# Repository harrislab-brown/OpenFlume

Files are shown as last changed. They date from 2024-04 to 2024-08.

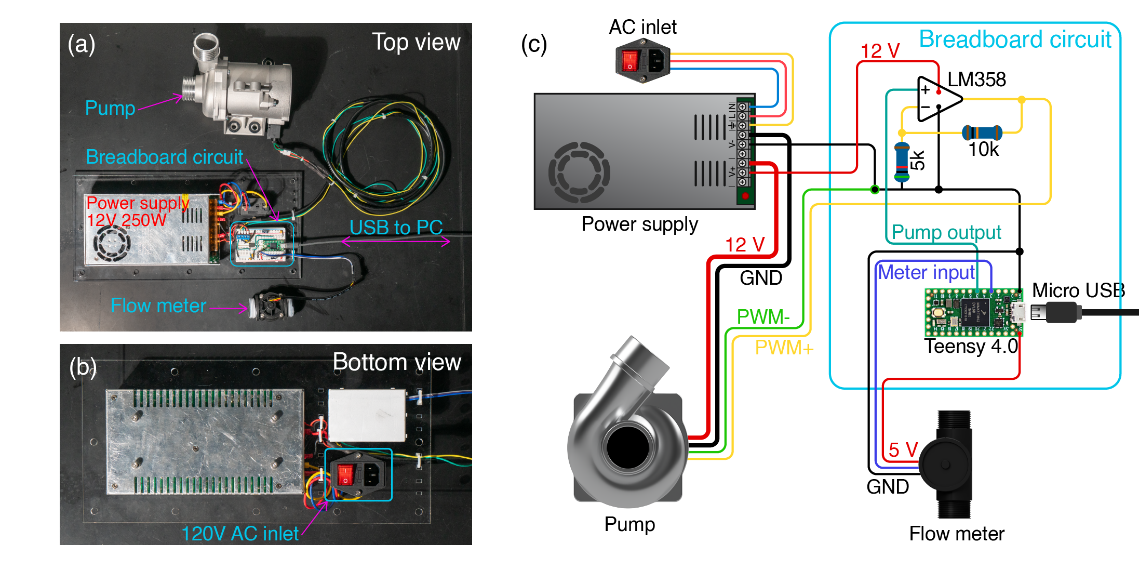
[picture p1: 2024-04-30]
Wiring Diagram/electronics_diagram3.png

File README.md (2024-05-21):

# OpenFlume
Low-cost benchtop laboratory flume for research and education with full build documentation released under an open-hardware license.

## What is OpenFlume?
OpenFlume is an open channel flume that features a 5x5cm flow test-section with free stream speeds upto 50 cm/s. It is as small as it can be while still allowing for ample flow conditioning prior to the test section. It has been fully characterized using Particle
Image Velocimetry. It is designed to be buildable with a range of tool access and skill levels. It uses the minimum viable product for its construction, keeping costs low without sacrificing quality. It is fully documented, so you 
can follow our instructions and build an OpenFlume to suit your needs. 

OpenFlume was designed by members of the Harris Lab and Brown University for experiments related to drag at the interface. To conduct these experiments, the lab needed a well controlled and uniform flow with low surface deviation. 
When looking at the commercial landscape for small scale flumes, the few small scale flumes that were available were expensive and lacked the full characterization needed for the lab to be confident in their direct applicability to research. 

## License:
OpenFlume is licensed under the CC BY-SA 4.0 Creative Commons license.

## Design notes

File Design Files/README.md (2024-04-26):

# OpenFlume

All of the 3D CAD and 2D cut files associated with the OpenFlume project.

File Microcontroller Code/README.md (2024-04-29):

# OpenFlume

This arduino sketch has been tested on a Teensy4.0 development board.
To use this code, follow the wiring diagram from the OpenFlume paper and make all appropriate connections with the Teensy. The Arduino IDE 2.x
has the ability to add additional board manager repositories. Follow the guide found at [PJRC Teensy4.0 Tutorial](https://www.pjrc.com/teensy/tutorial.html)
to get the Arduino IDE set up to flash the Teensy. Downlad the flume_controller.ino file and put it in a folder with the name flume_controller. This should allow you to open the arduino project in the IDE, compile, and flash the code.

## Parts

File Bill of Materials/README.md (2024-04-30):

# OpenFlume

Bill of materials for each subsystem can be found here. Open the .html files in a browser to view a static version of the BOM spreadsheets,
or find the same information in the .xlsx workbook for easier editability.

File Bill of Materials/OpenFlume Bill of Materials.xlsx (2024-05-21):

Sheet: Plumbing
Designator | Component | Quantity | Cost per Unit ($) | Total Price ($) | Source of Material | McMaster Carr Item Number
Plumbing | 1” Braided Vinyl Tubing | 4 ft | ($3.28 /ft.) | $13.12 | Home Depot
Plumbing | 1.5” Braided Vinyl Tubing | 4 ft | ($4.75 /ft.) | $19.00 | Home Depot
Plumbing | Bulkhead Fitting 1” NPT Female Thread 304 Stainless Steel Thru-bulk Fitting | 2 | ~10.00 | $19.99 | Amazon
Plumbing | PVC Barbed Tee Fitting - 1 PVC Tee Barb Fitting | 1 | $9.95 | $9.95 | Amazon
Plumbing | 1” NPT Gate Valve | 1 | $15.34 | $15.34 | Home Depot
Plumbing | High-Pressure Plastic Fitting (1.5” Barbed Male to 1.5” NPT Female) | 2 | $16.42 | $32.84 | McMaster Carr | 48315K113
Plumbing | High-Pressure Plastic Fitting (1.5” Barbed Male to 1” Barbed Male) | 2 | $8.01 | $16.02 | McMaster Carr | 48315K75
Plumbing | High-Pressure Plastic Fitting (1” Barbed Pipe × 1” NPT Male Threaded Pipe) | 4 | $2.47 | $9.88 | McMaster Carr | 48315K93
Plumbing | 1/2" Wide Teflon Tape | 1 | $3.97 | $3.97 | Amazon
Plumbing | Stainless Steel Hose Clamps (1 inch to 2 inch diameter) | 1 | $9.99 | $9.99 | Amazon
 |  |  | Total: | $150.10

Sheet: Electronics
Designator | Component | Quantity | Cost per Unit ($) | Total Price ($) | Source of Material | Part Number
Electronics | 1.5” Water Flow Sensor 5-150LPM | 1 | $26.99 | $26.99 | Amazon
Electronics | Teensy4.0 | 1 | $28.50 | $28.50 | Digikey | 1568-DEV-16997-ND
Electronics | S-250-12 Power Supply | 1 | $23.99 | $23.99 | Amazon
Electronics | LM358N Op-Amp | 1 | $0.89 | $0.89 | Digikey | LM358NNS/NOPB-ND
Electronics | Aftermarket CWA-200 BMW Coolant Pump | 1 | $118.99 | $118.99 | Amazon
Electronics | 15A 250V Rocker Switch Power Socket Inlet | 1 | $7.99 | $7.99 | Amazon
Electronics | Resistor Assortment 1/4W | 1 | $9.99 | $9.99 | Amazon
Electronics | Ceramic Capacitor Assortment | 1 | $9.99 | $9.99 | Amazon
Electronics | 14 AWG Silicone Wire 20' | 1 | $9.88 | $9.88 | Amazon
Electronics | Solderless Breadboard | 1 | $6.99 | $6.99 | Amazon
Electronics | Breadboard Hookup Wire assortment | 1 | $14.58 | $14.58 | Amazon
Electronics | Ring Terminal Assortment | 1 | $8.98 | $8.98 | Amazon
Electronics | Breadboard Screw Terminals | 1 | $8.99 | $8.99 | Amazon
Electronics | Micro USB Cable | 1 | $3.99 | $3.99 | Amazon
 |  | Total: | $280.74

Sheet: Aluminum Substructure
Designator | Component | Quantity | Cost per Unit ($) | Total Price ($) | Source of Material | McMaster Item Number | Material Type
Substructure | Silver Corner Surface Bracket for 1” High Single Rail | 10 | $11.60 | $116.00 | McMaster Carr | 47065T267
Substructure | Silver Flush 90 Degree Angle Bracket for 1” High Rail | 2 | $17.05 | $34.10 | McMaster Carr | 3136N157
Substructure | Silver Corner Surface Bracket 4” Long | 2 | $30.60 | $61.20 | McMaster Carr | 47065T274
Substructure | 1" Long for 1" High Rail T-Slotted Framing | 4 | $7.92 | $31.68 | McMaster Carr | 47065T236
Substructure | M5 x 0.8 mm Thread, 45 mm Long | 2 | $8.46 | $16.92 | McMaster Carr | 91292A195 | look up how many come with each order
Substructure | M5 x 0.8 mm Thread | 1 | $9.77 | $9.77 | McMaster Carr | 91828A241 | look up how many come with each order
Substructure | 18-8 Washer for M5 Screw Size, 5.300 mm ID, 9.000 mm OD | 1 | $4.00 | $4.00 | McMaster Carr | 98689A114 | look up how many come with each order
Substructure | 12” 1010-S from 80/20 | 4 | $6.99 | $27.96 | 80/20
Substructure | 5” (127 mm) 1010-S | 8 | $4.54 | $36.32
Substructure | 25” (635 mm) 1010-S | 2 | $11.54 | $23.08 | 80/20
Substructure | 21” (533.4 mm) 1010-S | 2 | $10.14 | $20.28 | 80/20
Substructure | 6.67” (169.42 mm) 1010-S | 2 | $5.12 | $10.24 | 80/20
Substructure | 8” (203.2 mm) 1020-S | 2 | $7.75 | $15.50 | 80/20
Substructure | 10” (254 mm) 1010-S | 4 | $6.29 | $25.16 | 80/20
 |  | Total: | $141.77

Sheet: Flume Body
Designator | Component | Quantity | Cost per Unit ($) | Total Price ($) | Source of Material | McMaster Item Number | Material Type
Flume Body | Plastic Straws | 1 | $8.99 | $8.99 | Donation |  | for flow straightening honeycomb
Flume Body | 9mm Thick Acrylic Sheet 96″ x 48″ | 1 | $190.00 | $190.00 | Polymershapes
Flume Body | Oil-Resistant Buna-N O-Ring Cord Stock, 3 mm Wide | 3 ft | $0.45/foot | $1.35 | McMaster Carr | 9679K14 | For o-rings at Flume flanges
Flume Body | 50A 0.5mm Thick Neoprene Sheet 12" × 12" | 1 | $6.71 | $6.71 | McMaster Carr | 85785K21 | For rubber washers at outlet tank flange
Flume Body | 5.5 mm Acrylic Sheet (48" x 24") | 2 | $66.40 | $132.80 | Canal Plastics
Flume Body | Weld-On #4 Adhesive (Pint) | 1 | $26.16 | $26.16 | Amazon
Flume Body | Wet Sandpaper Set | 1 | $12.99 | $12.99 | Amazon |  | Mimum grit of 60 needed, maximum grit of 2000 needed
Flume Body | 3 mm Acrylic Sheet (48" x 24") | 1 | $38.40 | $38.40 | Canal Plastics
Flume Body | Super Glue (25 gram) | 1 | $8.57 | $8.57 | Amazon
Flume Body | Masking Tape | 1 | $3.50 | $3.50 | Amazon
Flume Body | Stainless Steel M4 x 8 mm Screws | 1 | $8.18 (pack of 100) | $8.18 | McMaster | 91292A108 | for securing inlet diffuser - check length
Flume Body | Woven Wire Mesh Screen (20 mesh) | 1 | $6.99 | $6.99 | Amazon
Flume Body | Novus Plastic Polish Set (#1,#2,#3 2 ounce bottles) | 1 | $12.75 | $12.75 | Amazon
Flume Body | Stainless Steel M3 x 12 mm Screws | 1 | 6 (pack of 100) | $6.00 | McMaster Carr | 91292A114 | for securing mesh gate
Flume Body | Stainless Steel M5 x 45 mm Screws | 2 | 8.46 (pack of 25) | $16.92 | McMaster Carr | 91292A195 | for joining flume subassemblies
Flume Body | Stainless Steel M5 Washers | 1 | 4.00 (pack of 100) | $4.00 | McMaster Carr | 98689A114
Flume Body | Steel Hex M5 Nuts | 1 | 4.76 (pack of 100) | $4.76 | McMaster Carr | 90592A095
Flume Body | M5 Rubber Washers (11mm OD 1.6 mm thick) | 1 | 5.99 (pack of 100) | $5.99 | Amazon
Flume Body | Bio Sponge Filter Media Pad Foam Sponges,Cut-to-Size Foam 16.5"x3.5"x2" 2Pcs | 1 | $11.99 | $11.99 | Amazon
 |  |  | Total: | $507.05

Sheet: Tool List
Tool Name | Quantity
Cutting Tools
Table Saw | 1
Router Table | 1
Drill Press | 1
Band Saw | 1
Laser Cutter | 1
Orbital Sander | 1
Freud LU94M010: 10" Plastic Table Saw Blade | 1
1/2 in. x 1 in. Carbide Flush Trimming Router Bit | 1
1/2 in. x 1 in. Carbide Top-Bearing Flush Trim Router Bit | 1
Drill Bits for Plastic Norseman 7pc | 1
1/8” Straight Router Bit | 1
Assembly Tools
3-D Filament Printer | 1
Trigger Clamps (12"-24" Opening) | 2024-08-10
Hex Key Allen Wrench Set (Metric and SAE) | 1
72-Tooth Ratcheting Combination Wrench Set (Metric and SAE) | 1
Impact Driver | 1
Exacto Knife | 1
Ratcheting Flexible Tube Cutter | 1
Rounded Rubber Sanding Block | 1
Tweezers | 1
1/4" x 6" Round Steel Dowels
Tap and Drill Set | 1
Measuring Tools
Digital Calipers | 1
1 x 2 x 3 Block | 1
Combination Square | 1
Electronics and Wiring Tools
Soldering Iron | 1
Ring Terminal Crimper | 1
Multi-meter (recommended) | 1
Wire Stripper | 1

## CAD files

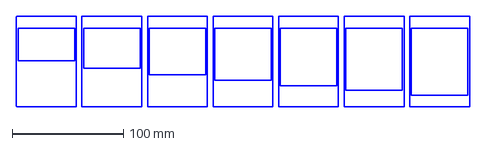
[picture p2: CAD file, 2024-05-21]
Design Files/weir gates.dxf
407.4 x 81.7 mm

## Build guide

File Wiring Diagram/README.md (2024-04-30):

# OpenFlume

Description of wiring procedure can be found in the OpenFlume paper. This repository contains a duplicate electronics diagram figure, as well as a KiCad 7.0
schematic of the breadboard circuit.

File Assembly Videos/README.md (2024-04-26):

# OpenFlume

Assembly videos were generated directly from the CAD files. They show the order in which pieces of each flume subsection were put together.

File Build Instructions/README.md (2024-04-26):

# OpenFlume
Narrative build instructions showing how each subassembly is put together. This includes discussion of the rational behind design decisions, overview of the tools and materials used, and documentation of the gluing and assembly procedures.

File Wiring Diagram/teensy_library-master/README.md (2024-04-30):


Donate using Liberapay (https://liberapay.com/xengi/donate)

Teensy symbol library for KiCAD
=======================================

This repo includes KiCAD symbols for the following Teensy versions:

  - Teensy 1.0
  - Teensy++ 1.0
  - Teensy 2.0
  - Teensy++ 2.0
  - Teensy 3.0
  - Teensy 3.1
  - Teensy 3.2
  - Teensy 3.5
  - Teensy 3.6
  - Teensy 4.0
  - Teensy 4.1
  - Teensy LC

There are two symbols for Teensy 3.5/3.6: one that includes the through-hole connections on Teensy and one that adds all of the SMT connections on the bottom of the Teensy.

For footprints look here: https://github.com/XenGi/teensy.pretty

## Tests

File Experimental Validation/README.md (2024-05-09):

# OpenFlume

Figures from our OpenFlume paper and data in CSV format used to generate them.

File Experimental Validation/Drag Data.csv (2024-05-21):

Sphere Size | Gate Height | Force (dynes) | Standard Deviation (dynes)
12p7 | 17 | 256.7951217 | 32.27245916
12p7 | 27 | 77.57278216 | 4.515455537
12p7 | 22 | 158.4813373 | 9.273705965
7p8 | 22 | 66.76377915 | 10.97169681
10 | 22 | 97.51888844 | 5.414745426

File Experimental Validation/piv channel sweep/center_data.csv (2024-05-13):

Average horizontal velocity (cm/s) | Standard deviation (cm/s)
23.592995435339 | 0.598576912102224
23.6373659755618 | 0.569778695249188
23.6600322042615 | 0.557598833585508
23.6932702617992 | 0.544627447361067
23.719503482461 | 0.566323784801264
23.7352134401309 | 0.582034741722106
23.7528559170551 | 0.583230330903011
23.7517530201414 | 0.630323482028525
23.7514860813966 | 0.663695222936639
23.776684276085 | 0.710146404307241
23.7843632129153 | 0.772954213293878
23.7796235669468 | 0.813961829881267
23.7738352968136 | 0.810168243312437
23.7509377796981 | 0.837967145892679
23.6967167744447 | 0.875770494904956
23.6538217395465 | 0.900255550303493
23.6143216687751 | 0.899810782770553
23.5717632107063 | 0.89115272949805
23.5497131676962 | 0.904766252318972
23.5343977875451 | 0.920738443668465
23.501613866605 | 0.912270101443842
23.4884012393583 | 0.928297197658845
23.4720302118806 | 0.957606854611458
23.4767711515429 | 0.990467460592492
23.4784638231996 | 1.00489192013289
23.4590060552943 | 0.993980668783399
23.4418550100112 | 0.949090797074255
23.4308693413536 | 0.941724515791066
23.4102764156045 | 0.925133360347009
23.3822646768088 | 0.909765546989264
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

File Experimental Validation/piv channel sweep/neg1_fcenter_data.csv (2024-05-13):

Average horizontal velocity (cm/s) | Standard deviation (cm/s)
23.0300579890502 | 2.24140140264639
23.3395871738822 | 2.04898557335298
23.5408516938823 | 2.13083278948606
23.6707435126768 | 2.26281823248854
23.7063077843928 | 2.59300032864558
23.7269017775916 | 2.58749958104853
23.7527720128883 | 2.32556929568461
23.7774309051247 | 2.22687564126404
23.7576547467222 | 2.51707549803582
23.7599823816573 | 2.35969012264029
23.7396463051986 | 2.64553758588946
23.7780893019208 | 2.41721061354091
23.779319748133 | 1.95405583741858
23.7643180448454 | 1.79836693134905
23.7442366621885 | 1.93548352382783
23.7206605062001 | 1.86343568810416
23.6683629801359 | 2.09738819654133
23.6234664755155 | 2.35979114476629
23.6161298811508 | 2.17328691533025
23.6116909780082 | 2.03717039633068
23.5992303371331 | 1.9349398350265
23.6007308123014 | 1.81507132008059
23.5928452835888 | 1.90894337367494
23.5580294761783 | 1.80680515598187
23.5159100899288 | 1.81225559802322
23.4670431521076 | 2.05992853067687
23.4664283675485 | 1.8848996820237
23.472819664863 | 1.85418495094544
23.4271165421667 | 2.33258368756298
23.4117337810149 | 2.29384800372985
23.3974563285924 | 2.16374898944451
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

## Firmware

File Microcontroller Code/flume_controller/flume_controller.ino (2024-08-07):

//#include <Arduino.h>

#define PIN_flow_meter 3
#define PIN_pump_pwm 5

const int PWM_RESOLUTION = 10; // 10 bit resolution for the PWM output
const long PWM_MAX_VAL = (1 << PWM_RESOLUTION) - 1;
const float MIN_DUTY = 0.16; // 0.16 is the measured duty cycle for pump to run at lowest speed
const float MAX_DUTY = 0.95; // 0.90 is the measured duty cycle for pump to run at full speed
float curr_duty_cycle = 0;
const float pump_init_val = 25.0;

unsigned prev_time = 0;
unsigned long dT = 0;
const long MIN_dT = 2000; // minimum time between rising edge pulses that will be considered. With our flow meter, a
                          // dT of 2000 would corrispond to a flow rate of 1000 l/min, much higher than the flow meter max of 150LPM

const byte window_size = 25; // Moving average window size

static byte curr_i = 0;    // Index for current value
static byte val_count = 0; // Count of values read (<= window_size)
static float sum = 0;      // Rolling sum
static float values[window_size];

void flow_meter_pulse();
void set_pump(float duty_cycle);
void wake_pump();

void setup()
{
  Serial.begin(115200);
  pinMode(PIN_flow_meter, INPUT_PULLDOWN);
  pinMode(PIN_pump_pwm, OUTPUT);
  analogWriteRes(PWM_RESOLUTION);

  attachInterrupt(digitalPinToInterrupt(PIN_flow_meter), flow_meter_pulse, RISING);

  wake_pump();

  set_pump(pump_init_val);

  prev_time = micros();
}

void loop()
{
  if (Serial.available())
  {
    float new_duty_cycle = Serial.parseFloat(); // read new duty cycle from user as percent (0.00-100.00)

    set_pump(new_duty_cycle); // set duty cycle as a percent, to be converted to an int by set_pump()
  }
  delay(1);
}

void wake_pump()
{
  // pump needs short pulse to wake up:
  delay(10);
  digitalWrite(PIN_pump_pwm, LOW);
  delay(10);
  digitalWrite(PIN_pump_pwm, HIGH);
  delay(10);
  digitalWrite(PIN_pump_pwm, LOW);
  delay(10);
  set_pump(pump_init_val);
}

void set_pump(float duty_cycle)
{

  int duty_cycle_100 = (int)(duty_cycle * 100.0);                                  // multiply float by 100 before converting to capture 2 decimal places
  long analog_write_val_100 = map(duty_cycle_100, 0, 10000, 0, PWM_MAX_VAL * 100); // mapped ranges are 100x for same reason
  long analog_write_val = analog_write_val_100 / 100;                              // divide by 100 to return to the range accepted by analogWrite()

  if (analog_write_val >= MIN_DUTY * PWM_MAX_VAL && analog_write_val <= MAX_DUTY * PWM_MAX_VAL)
  { // check if the set value is in bounds
    analogWrite(PIN_pump_pwm, analog_write_val);
    curr_duty_cycle = duty_cycle;
  }else if(analog_write_val == 0)
  { // ignore line end characters. \r\n returns 0 from Serial.parseFloat()
    return;
  }
  else
  { 
    Serial.printf("Pump duty cycle must be between [%.2f - %.2f]\n", MIN_DUTY * 100, MAX_DUTY * 100); // allert user if set value is out of bounds
  }
}

void flow_meter_pulse()
{
  unsigned long curr_time = micros();
  long dT = curr_time - prev_time;

  // guard to catch double trigger events from bounce in the flow meter signal
  if (dT < MIN_dT)
    return;

  // beginning of dT windowed average calculation:
  sum += dT;
  // If the window is full, adjust the sum by deleting the oldest value
  if (val_count == window_size)
    sum -= values[curr_i];

  values[curr_i] = dT; // Replace the oldest with the latest

  if (++curr_i >= window_size)
    curr_i = 0;

  if (val_count < window_size)
    val_count += 1;

  // final calculation of average dT from the sum of 'window_size' previous dT measurements
  float dT_avg = sum / val_count;

  float freq = 1000000.0 / dT; // convert between signal period (dT) in microseconds to frequency in Hz
  float freq_avg = 1000000.0 / dT_avg;

  // print result. Print statement runs much faster than the flow meter can spin and no issues with printing from the ISR have been observed
  Serial.printf("Time_(s):%012.6f\tPump_percent:%.2f\tInst._flow_rate(LPM):%05.2f\tAvg._flow_rate(LPM):%05.2f\n",
            curr_time / 1000000.0, curr_duty_cycle, freq * 2, freq_avg * 2);

  // update time for next dT calculation
  prev_time = curr_time;
}

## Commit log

2024-04-29 added Teensy code and installation instructions in the README
2024-04-30 added KiCad wiring diagram schematic
    [OpenFlume_Electronics.kicad_pcb, OpenFlume_Electronics.kicad_sch]
2024-04-30 added README and wiring diagram from paper
2024-04-30 added bill of materials and wrote BOM readme
    [OpenFlume Bill of Materials.xlsx]
2024-05-13 data upload
    [09_gate_data.csv, 13_gate_data.csv, 17_gate_data.csv, 22_gate_data.csv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]
2024-05-17 Create Drag Data.csv
    [Drag Data.csv]
2024-05-20 weir gates dxf upload
    [weir gates.dxf]
2024-05-21 updated BOM, removed html sheets, added pump datasheet and pwm info
    [OpenFlume Bill of Materials.xlsx]
2024-08-07 changed print output so it can be plotted with arduino serial plotter
